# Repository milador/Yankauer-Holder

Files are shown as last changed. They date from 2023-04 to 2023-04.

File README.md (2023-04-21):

# Yankauer-Holder
A simple solution based on Neodymium Magnets to keep Yankauer suction tip clean and prevent it from falling down.

## Demo

[Yankauer-Holder](https://www.youtube.com/shorts/TsDRbu0aiWg)

## Design

<p align="center">
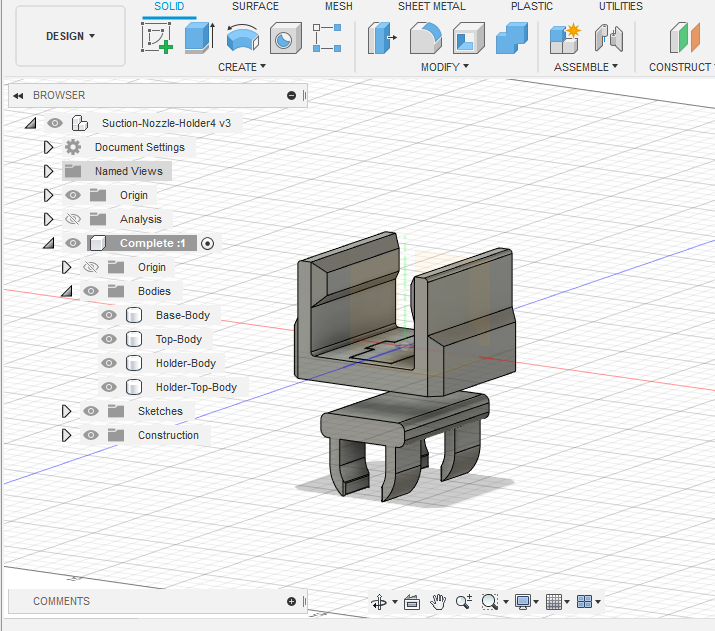
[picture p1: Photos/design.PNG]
Yankauer-Holder

</p>

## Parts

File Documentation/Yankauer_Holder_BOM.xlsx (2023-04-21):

Device: Yankauer-Holder |  |  | Total Cost | Total Print time (hr) | Total filament (g)
Version: V1.0 | Date Created: 04/20/2023 |  | $3.02 | 2.18 | 22.33
Commercial Parts:
Part type | Part Name | Part Label | Quantity Needed | Pkg Quantity | Price per package | Price per Unit | Price for qty needed | Link | Alternate Links
Mechanical | 30x10x3-4MM Neodymium Rectangle Magnet |  | 2 | 1 | $1.25 | $1.25 | $2.50 | https://vi.aliexpress.com/item/1005005115331365.html
 |  |  |  |  |  | $1.25
3D Printed Parts ESTIMATED PRICING USING 1KG ROLL COST: | $25.00
Part | Description |  | Quantity Needed | TOTAL Mass (g) | Estimated Price | Print Time (Min) | Link
Yankauer-Holder-Base | 15% Infill |  | 1 | 13.42 | $0.34 | 77 | https://github.com/milador/Yankauer-Holder/blob/main/Build_Files/3D_Print_Files/STL/Yankauer-Holder-Base.stl
Yankauer-Holder-Clip | 15% Infill |  | 1 | 6.13 | $0.15 | 46 | https://github.com/milador/Yankauer-Holder/blob/main/Build_Files/3D_Print_Files/STL/Yankauer-Holder-Clip.stl
Yankauer-Holder-Top | 15% Infill |  | 2 | 1.39 | $0.03 | 8 | https://github.com/milador/Yankauer-Holder/blob/main/Build_Files/3D_Print_Files/STL/Yankauer-Holder-Top.stl

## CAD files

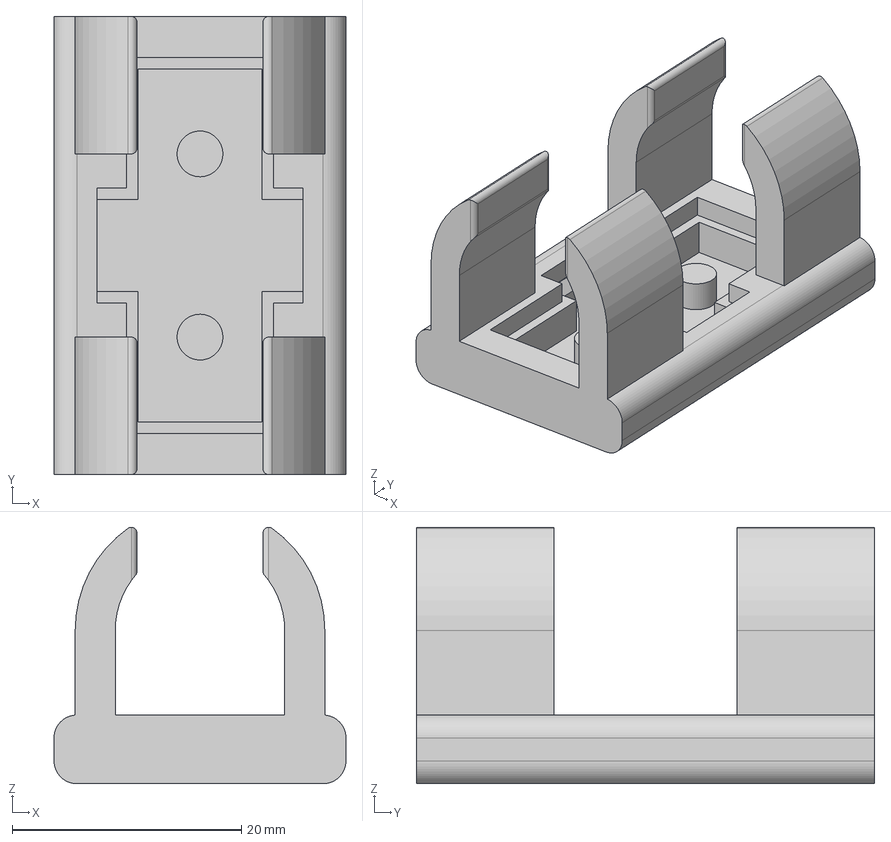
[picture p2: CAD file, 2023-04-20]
Build_Files/3D_Print_Files/STEP/Yankauer-Holder-Clip.step
25.5 x 40.0 x 22.4 mm

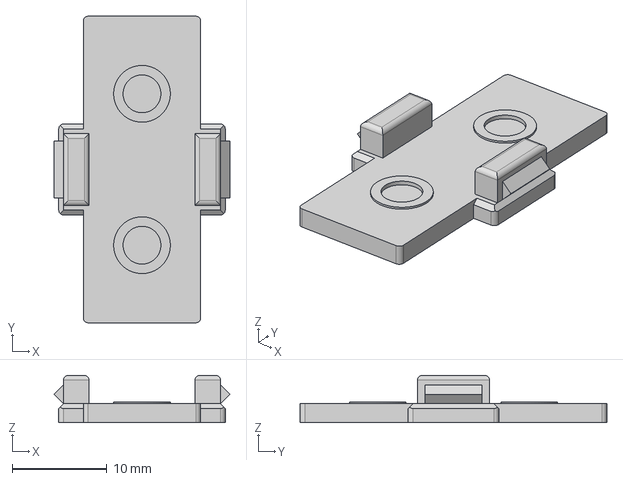
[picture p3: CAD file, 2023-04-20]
Build_Files/3D_Print_Files/STEP/Yankauer-Holder-Top.step
18.6 x 32.4 x 5.00 mm

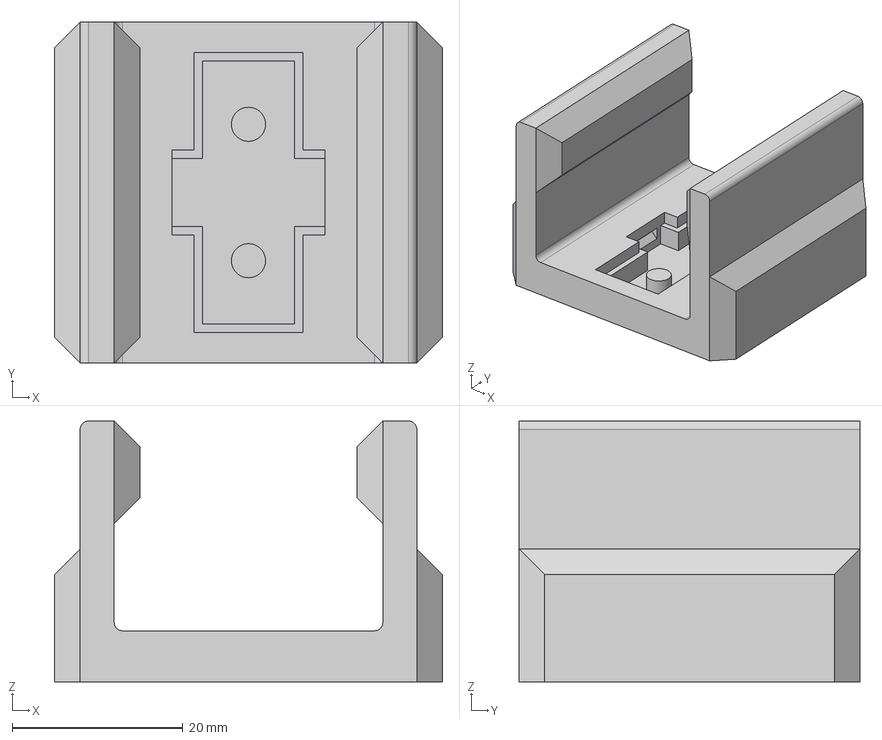
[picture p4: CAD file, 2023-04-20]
Build_Files/3D_Print_Files/STEP/Yankauer-Holder-Base.step
45.5 x 40.0 x 30.6 mm

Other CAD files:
Build_Files/3D_Print_Files/STL/Yankauer-Holder-Base.stl
Build_Files/3D_Print_Files/STL/Yankauer-Holder-Clip.stl
Build_Files/3D_Print_Files/STL/Yankauer-Holder-Top.stl
Design_Files/CAD/Yankauer-Holder.f3d

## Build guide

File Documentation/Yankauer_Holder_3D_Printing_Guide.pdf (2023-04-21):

V1.0 | April 2023

## Yankauer-Holder

## 3D PRINTING GUIDE V1.0

### 3D Printing Summary

Metrics | V1.0
Total Print Time (min) | 138
Total Number of Components | 4
Typical Total Mass (g) | 22.33
Typical Number of Print Setups | 1

### 3D Printing Settings

Print File Name | Qty | Total Print Time (hr:min) | Mass (g) | Infill (%) | Support (Y/N) | Layer Height/ Nozzle Diameter (mm) | Notes (orientation, special settings, etc.)
Yankauer-Holder-Base.stl | 1 | 1:17 | 13.4 2 | 15 | N | 0.2/0.4
Yankauer-Holder-Clip.stl | 1 | 0:46 | 6.13 | 15 | N | 0.2/0.4
Yankauer-Holder-Top.stl | 2 | 0:08 | 1.39 | 15 | N | 0.2/0.4

### 3D Printing Settings

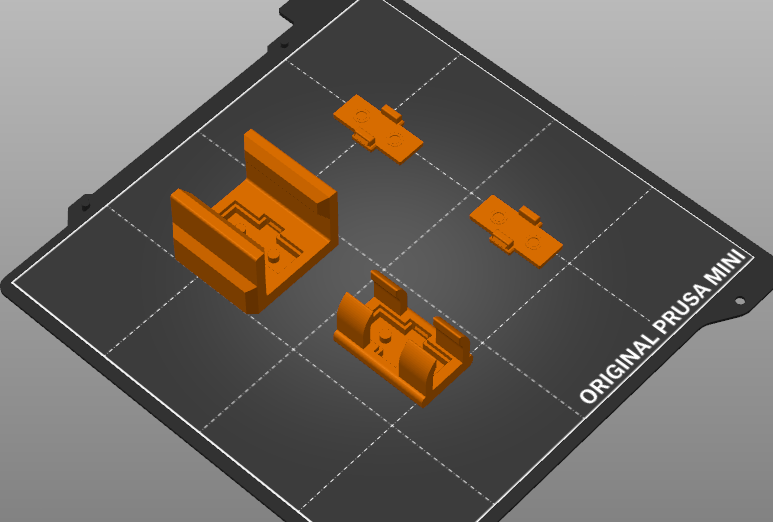
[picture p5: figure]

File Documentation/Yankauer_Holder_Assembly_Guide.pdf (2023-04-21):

V1.0 | April 2023

## Yankauer-Holder

## ASSEMBLY GUIDE V1.0

### Required Components

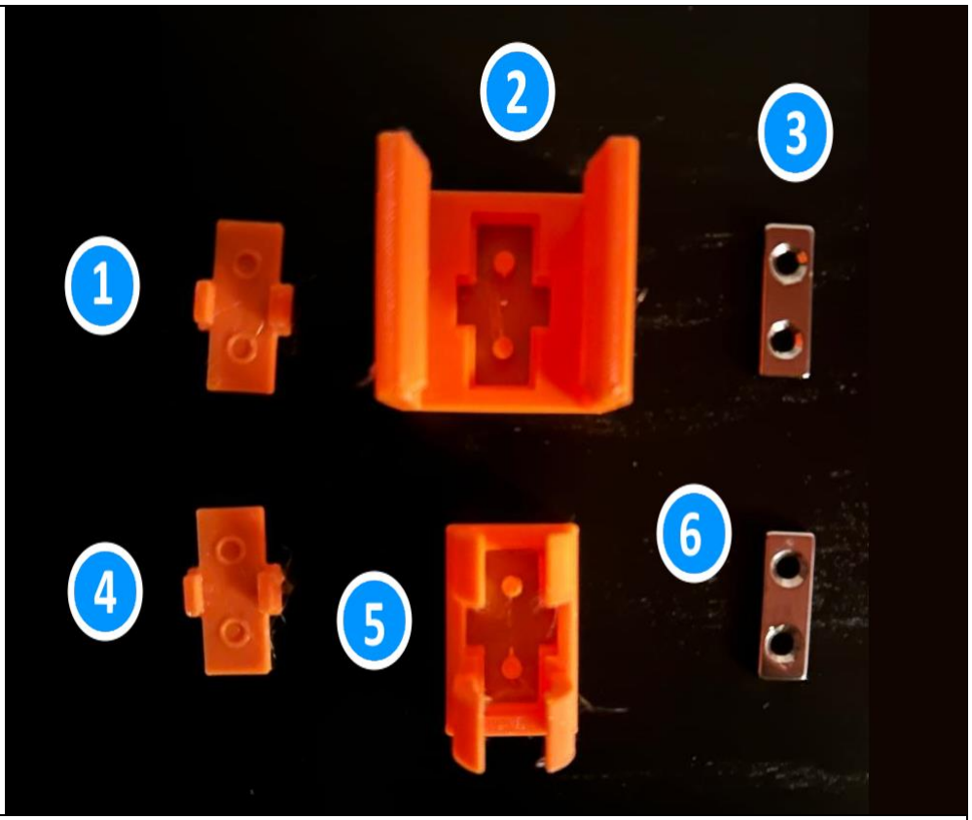
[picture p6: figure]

BOM
1. 1X 3D Printed Yankauer-Holder-Top Case
2. 1X 3D Printed Yankauer-Holder-Base Case
3. 1X 30x10x3-4MM Neodymium Rectangle Magnet
4. 1X 3D Printed Yankauer-Holder-Top Case
5. 1X 3D Printed Yankauer-Holder-Clip Case
6. 1X 30x10x3-4MM Neodymium Rectangle Magnet

## ASSEMBLY GUIDE V1.0

### Required Tools

- Side cutters

## ASSEMBLY GUIDE V1.0

### Assembly Instructions

### Step 1

Prepare parts to assemble Base component. These parts include a Neodymium magnet, a Yankauer-Holder-Top case, and a Yankauer-Holder-Base case.

### Step 2

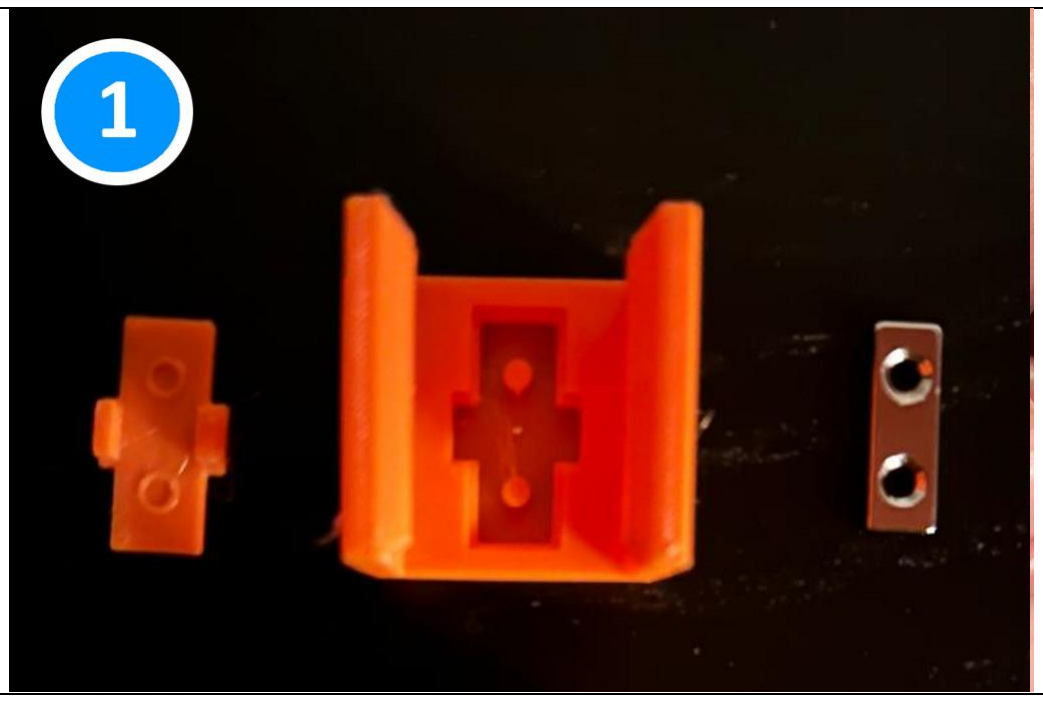
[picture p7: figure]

Place the Neodymium magnet firmly onto the Base component section. Ensure the posts of the base go through the two holes of the magnet.

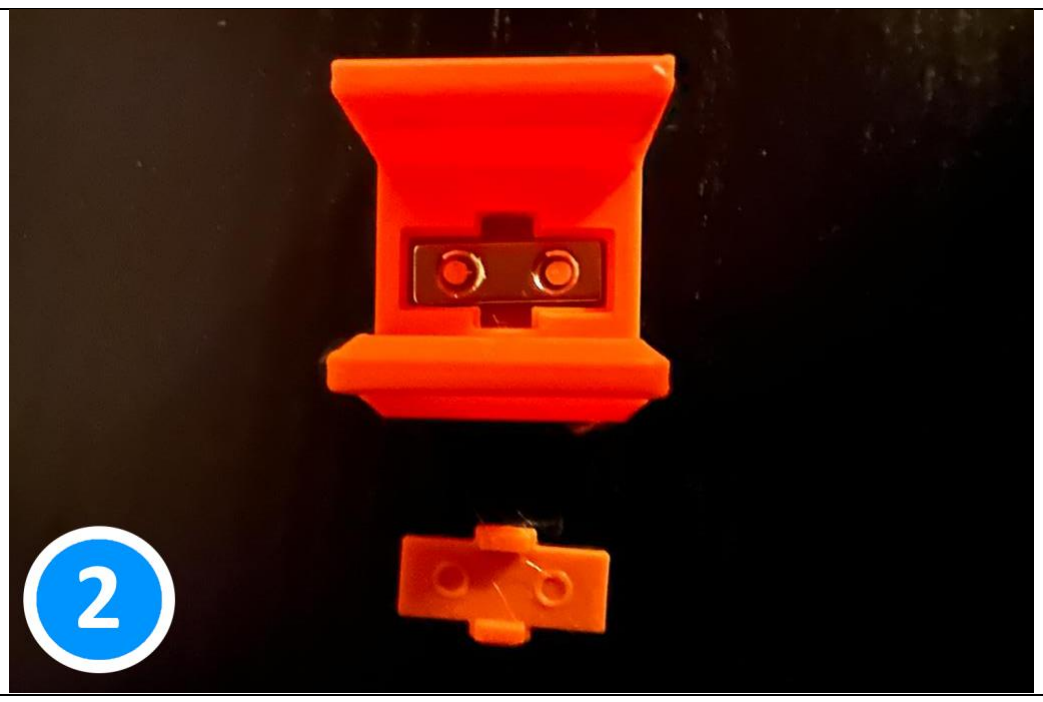
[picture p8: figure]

## ASSEMBLY GUIDE V1.0

### Step 3

Clip the posts of Yankauer-Holder-Top case onto the Yankauer-Holder-Base case, as shown in the image below.

### Step 4

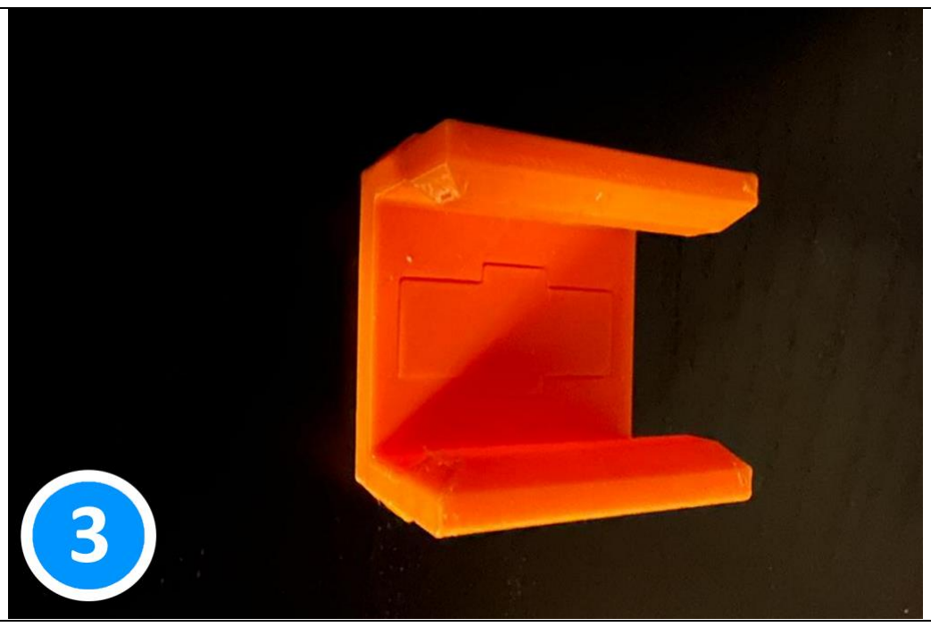
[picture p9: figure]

Prepare parts to assemble clip component. These parts include a Neodymium magnet, a Yankauer-Holder-Top case, and a Yankauer-Holder-cClip case.

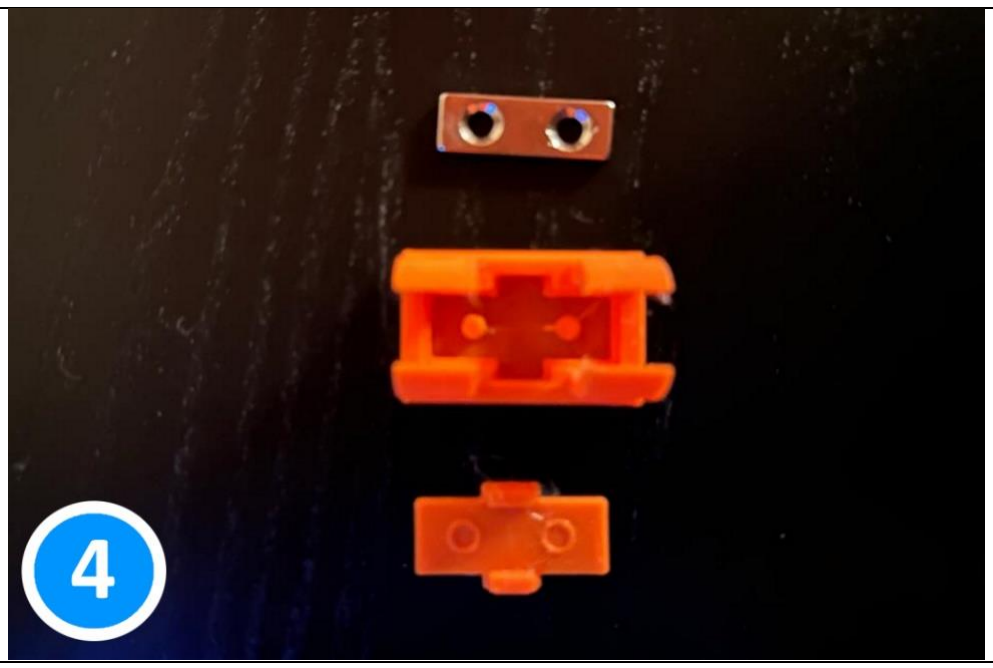
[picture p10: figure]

## ASSEMBLY GUIDE V1.0

### Step 5

Place the Neodymium magnet firmly onto the Clip component magnet section. Ensure the posts of the Clip go through the two holes of the magnet.

### Step 6

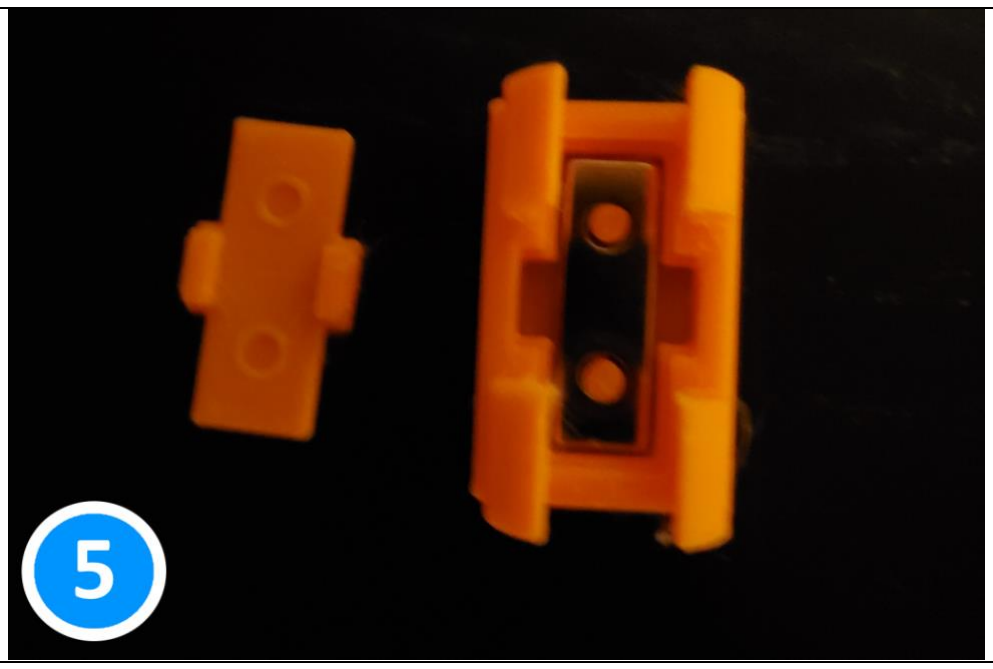
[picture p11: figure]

Clip the posts of Yankauer-Holder-Top case onto the Yankauer-Holder-Clip case, as shown in the image below.

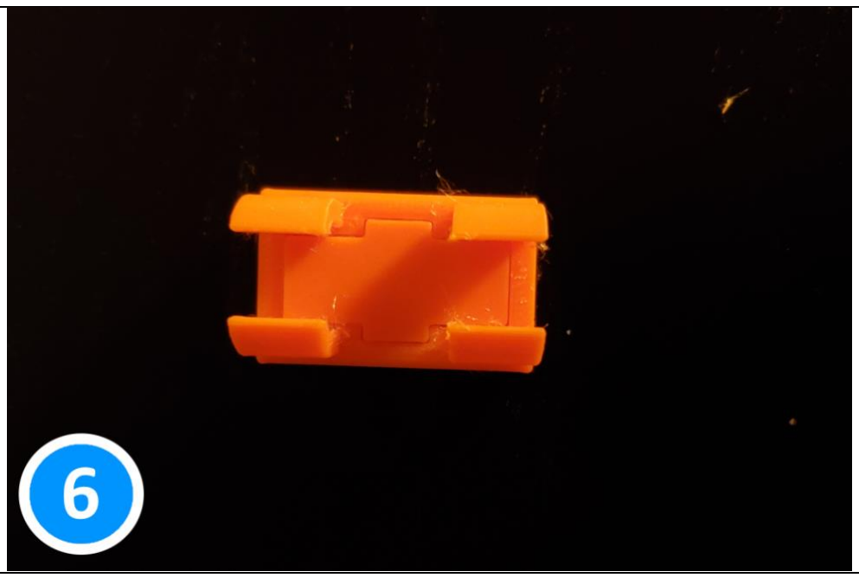
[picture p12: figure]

## ASSEMBLY GUIDE V1.0

### Step 7

The Yankauer-Holder base and clip assembly process is now complete.

### Step 8

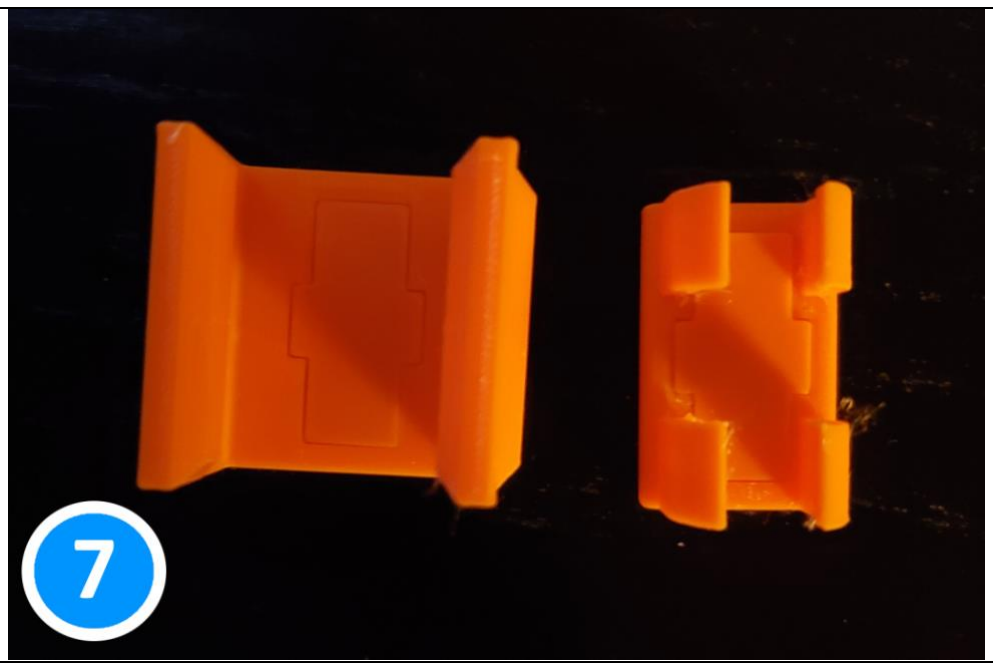
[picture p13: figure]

The Yankauer-Holder is being used to prevent suction tip to fall on the ground.

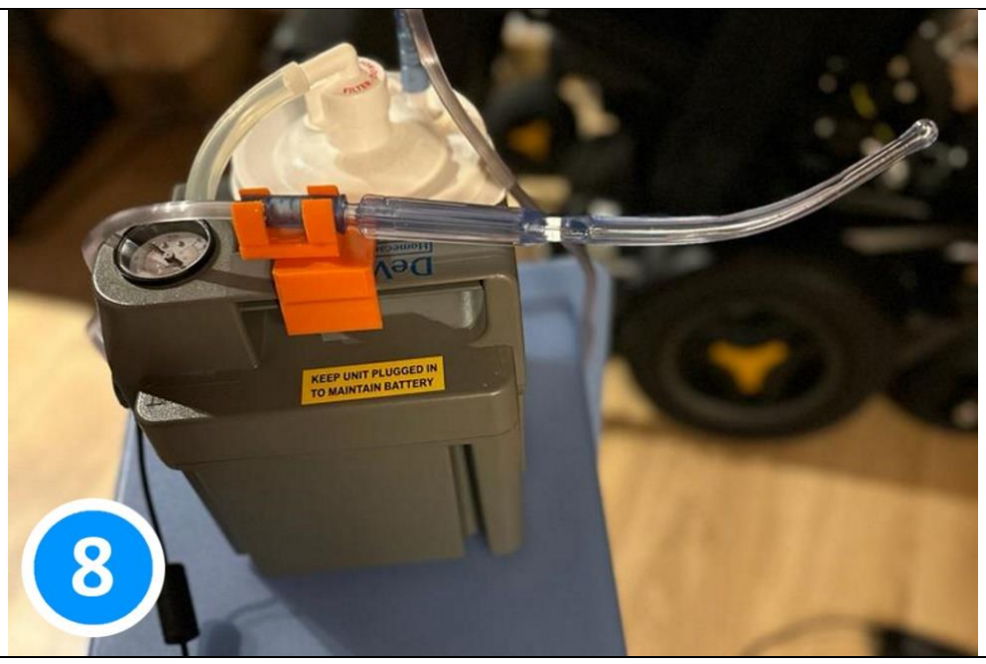
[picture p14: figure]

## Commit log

2023-04-20 Initial push
    [Yankauer-Holder-Base.step, Yankauer-Holder-Base.stl, Yankauer-Holder-Clip.step, Yankauer-Holder-Clip.stl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]
2023-04-21 Added assembly instructions
    [Yankauer_Holder_BOM.xlsx]
